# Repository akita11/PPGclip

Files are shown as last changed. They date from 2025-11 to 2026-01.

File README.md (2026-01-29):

# PPG Clip

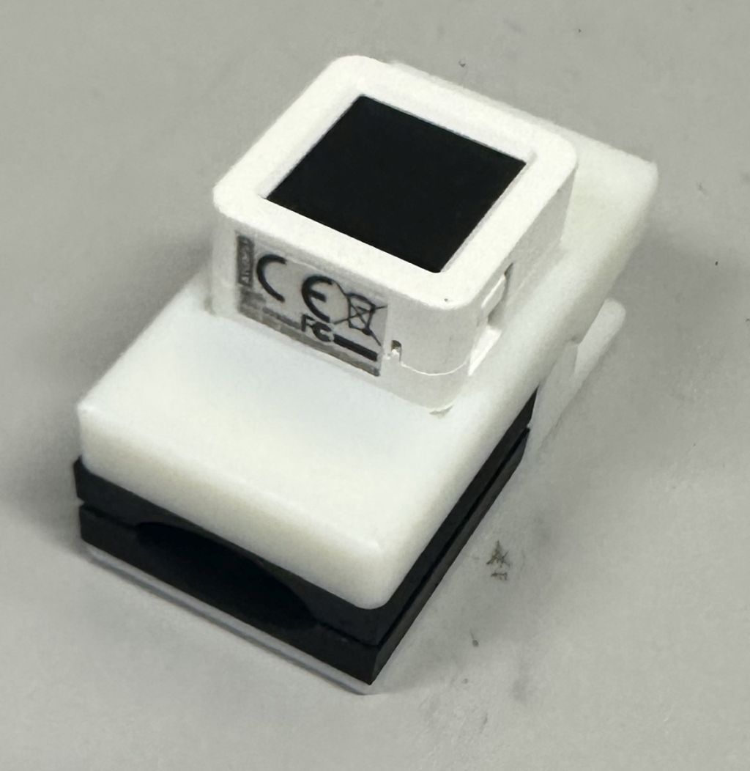
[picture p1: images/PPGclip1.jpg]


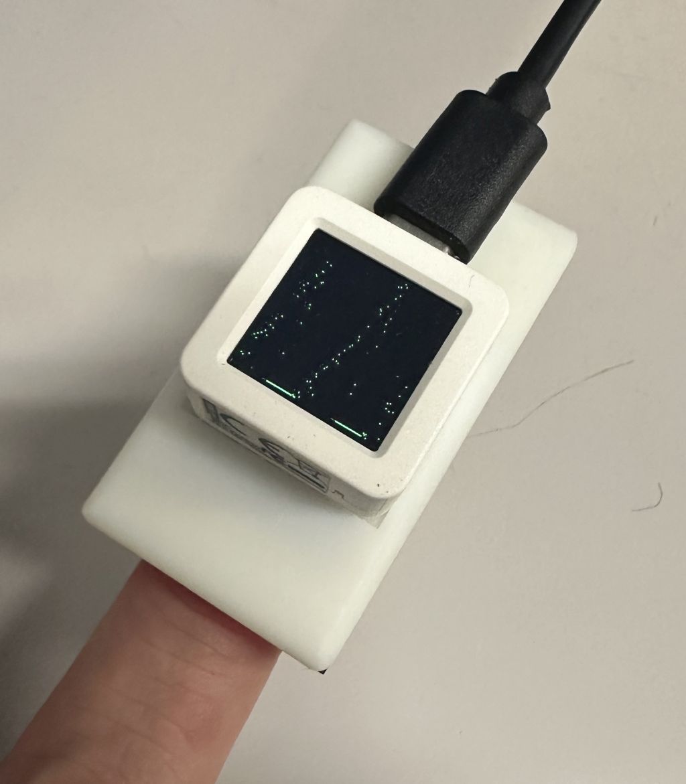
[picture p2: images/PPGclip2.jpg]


[M5Stack社の心拍センサユニット](https://www.switch-science.com/products/5695)を利用した、測定精度・安定度の高い透過型の光学脈波(PPG)計測器です。
マイコン部はM5Stack社のATOMシリーズを取り付けらて一体化できます。
部品セットからこれらを組み立てることができます。

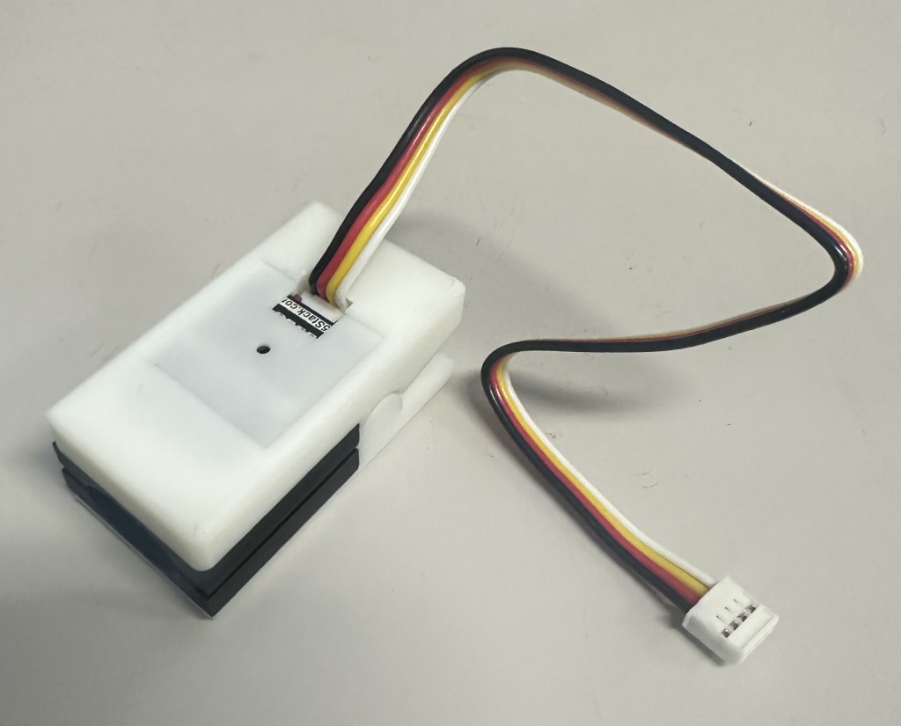
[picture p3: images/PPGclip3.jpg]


ATOMシリーズを使わずに、直接Groveケーブルを接続して、他のM5Stackシリーズ等のマイコンで使用することもできます。

## 必要なもの
- 部品セット（筐体（4点）、LED基板、コネクタ基板、4p/2mmピンソケット×2、ケーブル（色が写真のものと異なる場合があります）、M2.3×8mmタッピングねじ、M2×4mmねじ、押しバネ0.7×7.5×23）
- [M5Stack社の心拍センサユニット](https://www.switch-science.com/products/5695)
- M5Stack社ATOMシリーズ（ディスプレイのついている[ATOMS3](https://www.switch-science.com/products/8670)が脈波確認などができて便利。ATOMS3用のサンプルファームウエアあり）
- 工具（1.5mm六角レンチ、小プラスドライバ）

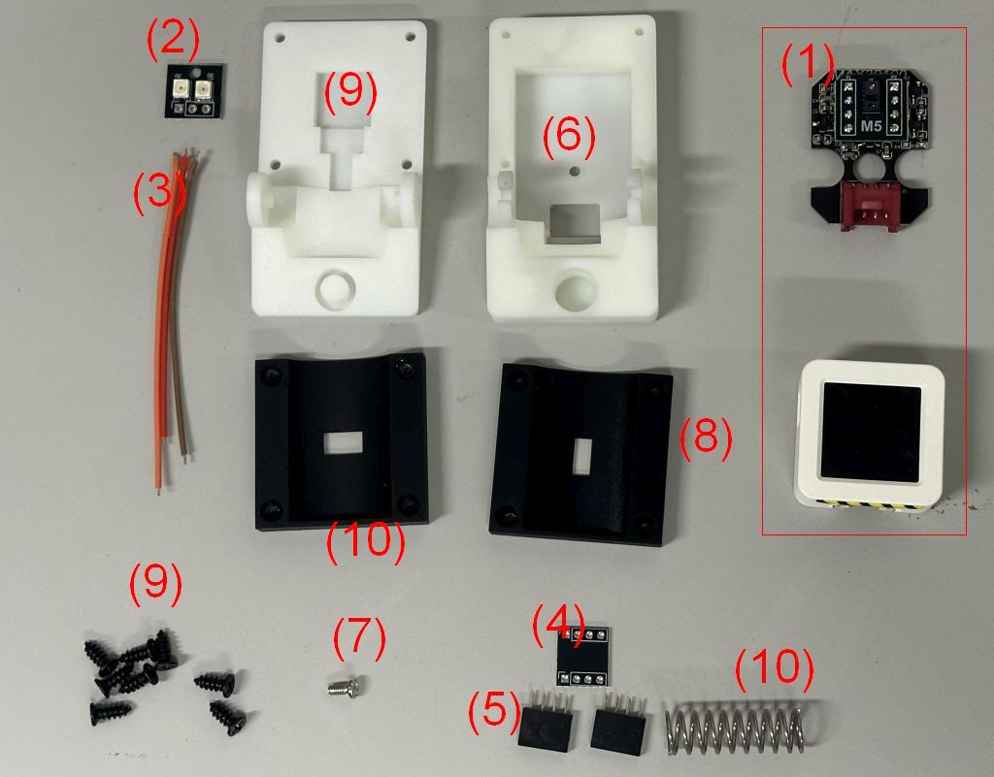
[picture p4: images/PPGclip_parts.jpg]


# 組み立て

1. 心拍センサユニットを、1.5mm六角レンチを使って分解し、中のボード(1)を取り出します。
1. LED基板(2)とボード(1)を、ケーブル(3)でFig1のようにはんだ付けして接続します。ケーブルの対応関係を間違えないように注意してください。このとき、ボード(1)側は、ケーブルを横側に引き出し、はんだづけ箇所がなるべく平坦になるようにします。
1. コネクタ基板(4)に、4p/2mmピンソケット(5)を2個、傾かないように注意してはんだ付けし、足をなるべく短くカットします。（Fig2）
1. ボード(1)にコネクタ基板(4)を差し込み、Fig3のように筐体(6）にはめます。ケーブル(3)は、図のように上面基板に重ならないようにします。
1. ATOMシリーズを、コネクタ基板(4)の反対側にさしこみ、M2ねじ(7)でFig3のように固定します。
1. 黒い筐体(8)を筐体(6)（向きに注意）に、4個のタッピングねじ(9)でFig4のように固定します。
1. 筐体(9)に、LED基板(2)をFig5のようにはめ、黒い筐体(10)（向きに注意）を、4個のタッピングねじ(9)でFig6のように固定します。
1. Fig7のように、ばね(10)を筐体(9)にはめ、その後、Fig8のように、ばね(10)を反対側の筐体(6)にはめつつ、2つの筐体を押し込んではめこみます。
1. ATOMシリーズにプログラムを書き込み、ボード(1)が動作すると、Fig9のように上下両側のLEDが点灯します。

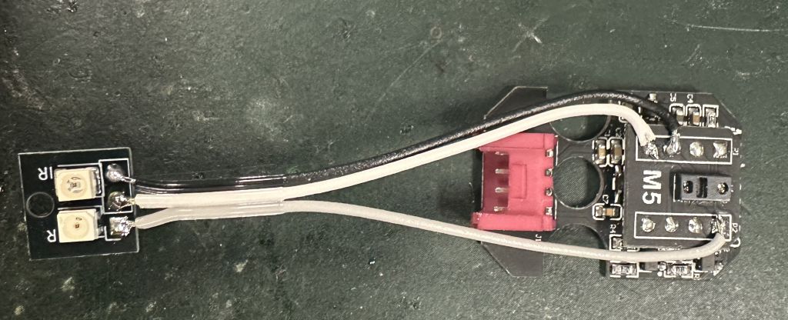
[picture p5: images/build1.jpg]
Fig1.:

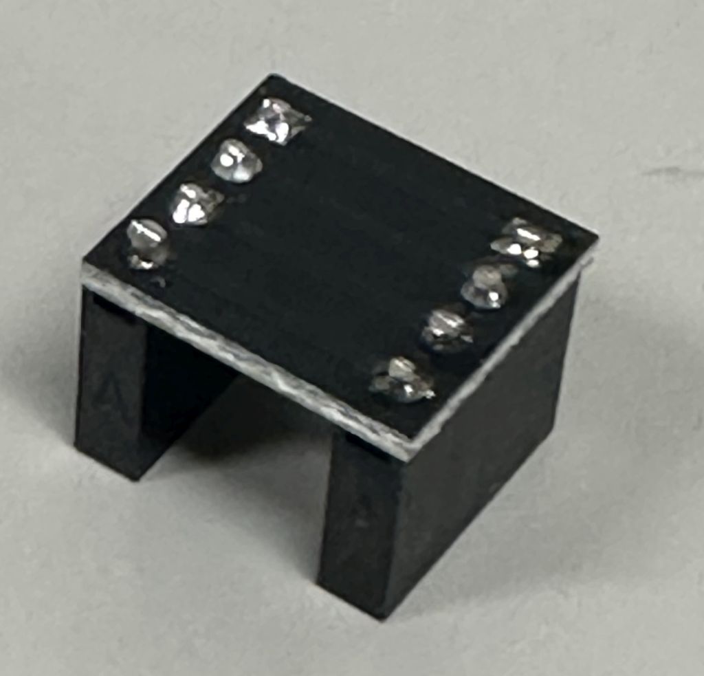
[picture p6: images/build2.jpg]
Fig2:

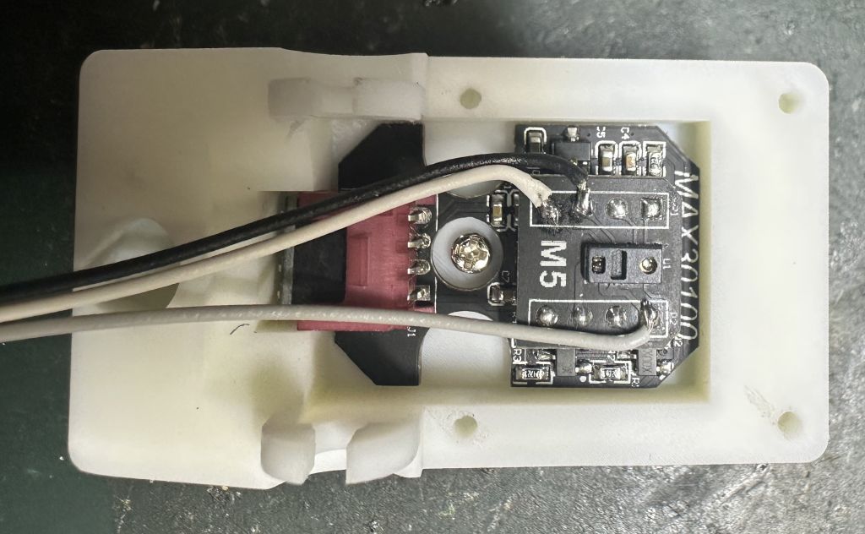
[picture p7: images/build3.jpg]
Fig3:

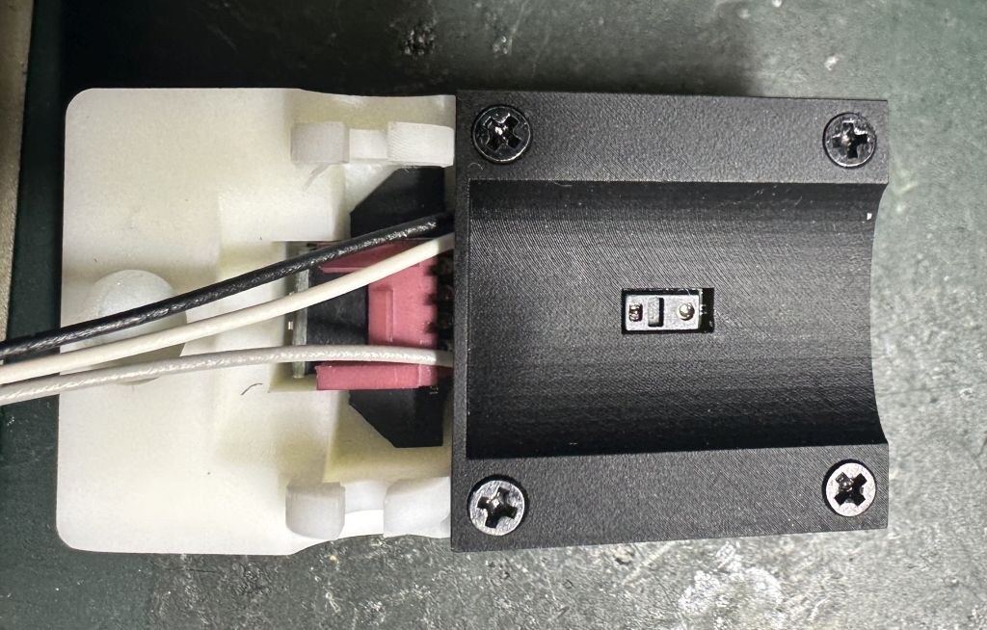
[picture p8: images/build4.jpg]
Fig4:

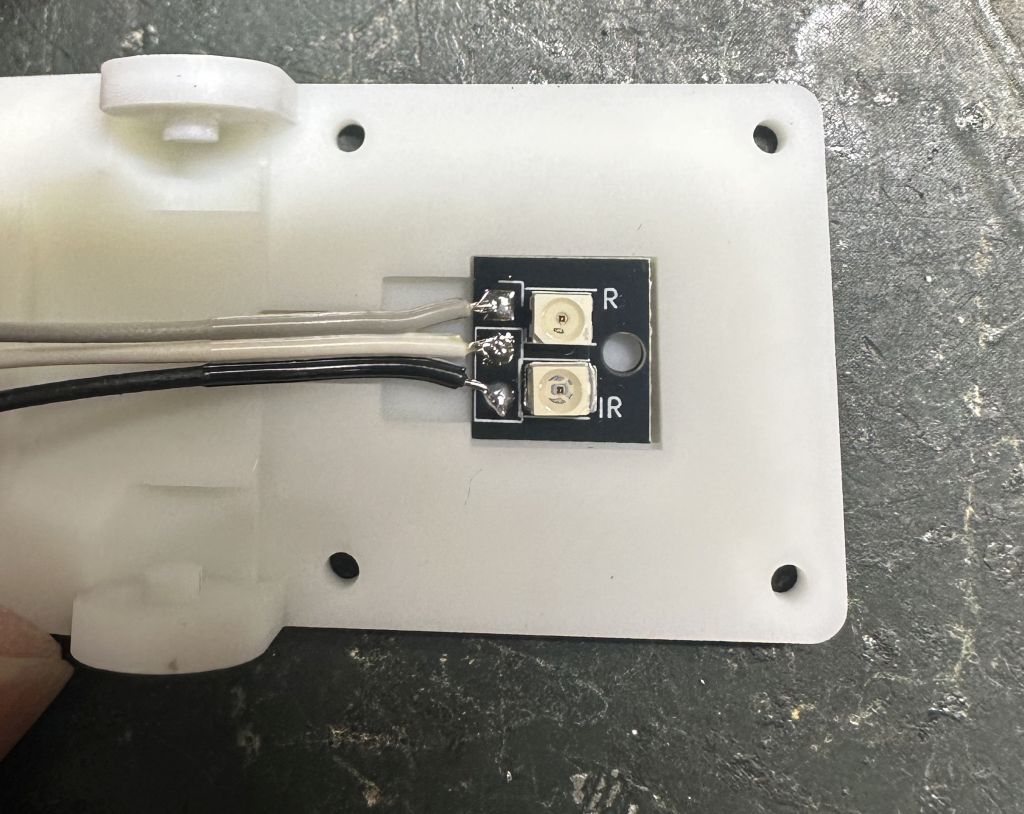
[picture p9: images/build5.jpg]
Fig5:

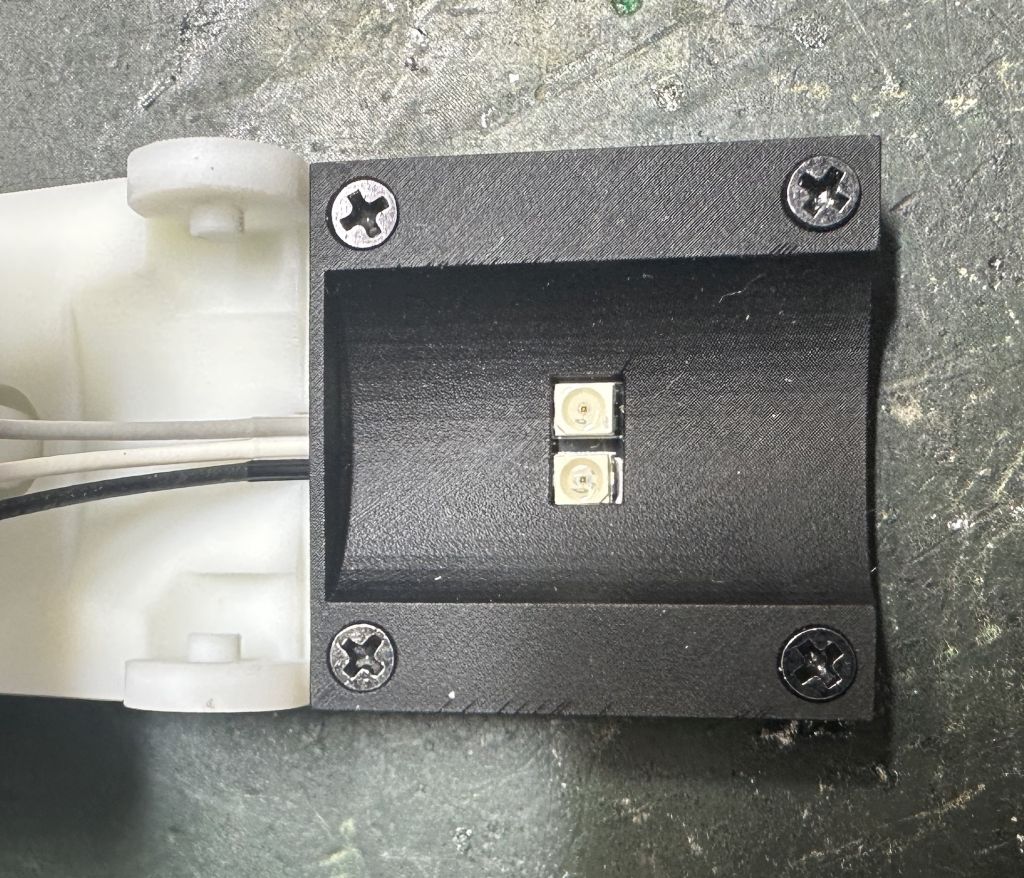
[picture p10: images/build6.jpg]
Fig6:

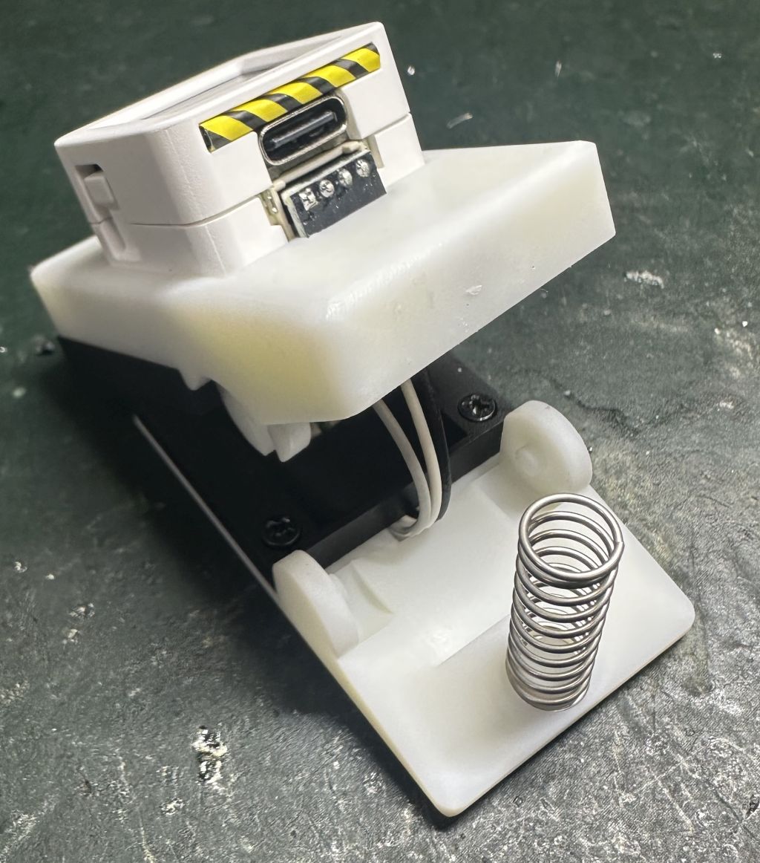
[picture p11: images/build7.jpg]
Fig7:

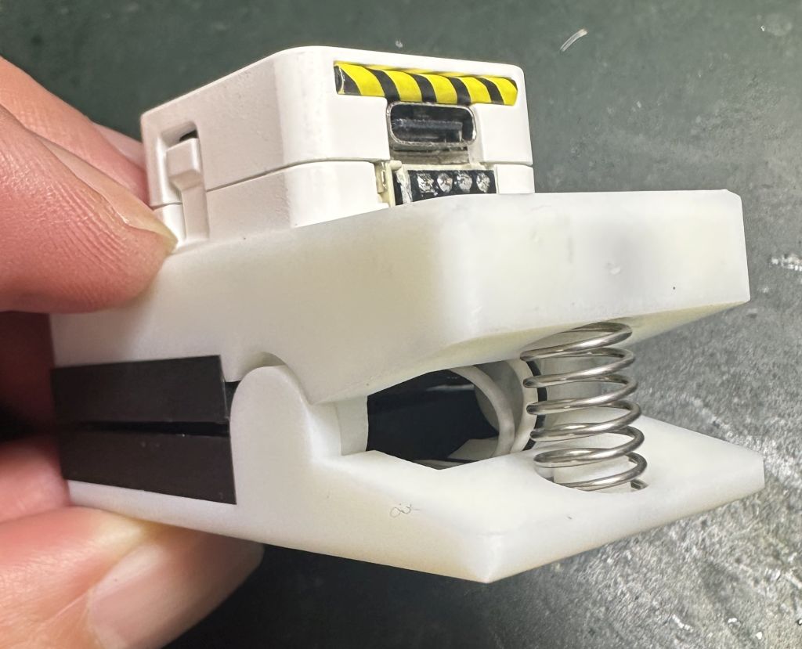
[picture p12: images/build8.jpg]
Fig8:

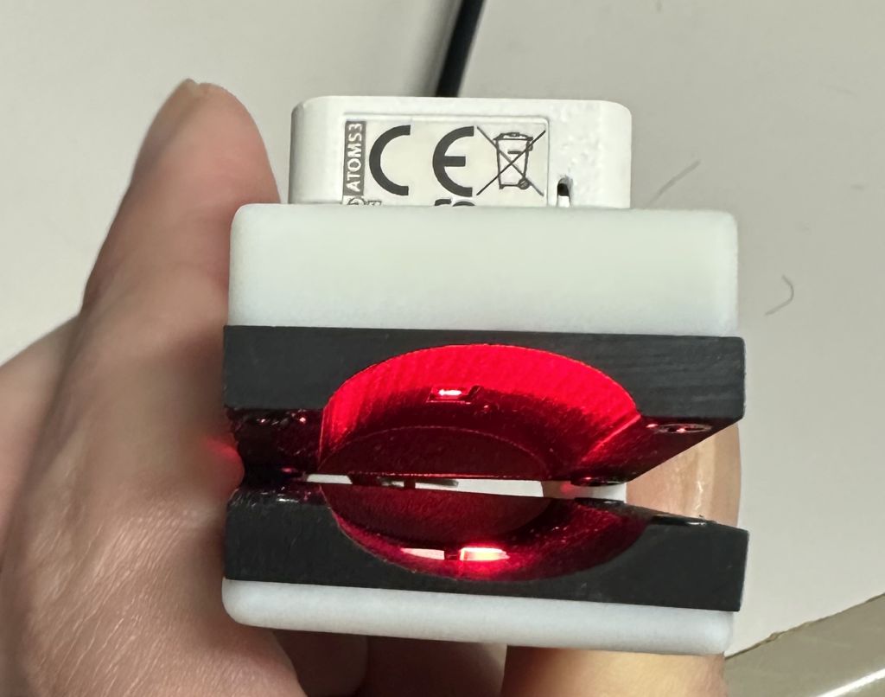
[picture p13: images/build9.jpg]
Fig9:

# ソフトウエア

M5Stack社の心拍センサユニット用のプログラムはすべて利用できます。サンプルとして、以下の機能をもつATOMS3用のプログラムがsampleFW/内にあります。
- 波形表示(100Hzサンプリング)
- ベースライン変動除去
- 簡易な正常計測チェック（正常計測時は緑色のグラフ）
- ボタンを押すと10秒分の生データをUSU UARTにCSV形式で出力

## Author

Junichi Akita (@akita11) / akita@ifdl.jp

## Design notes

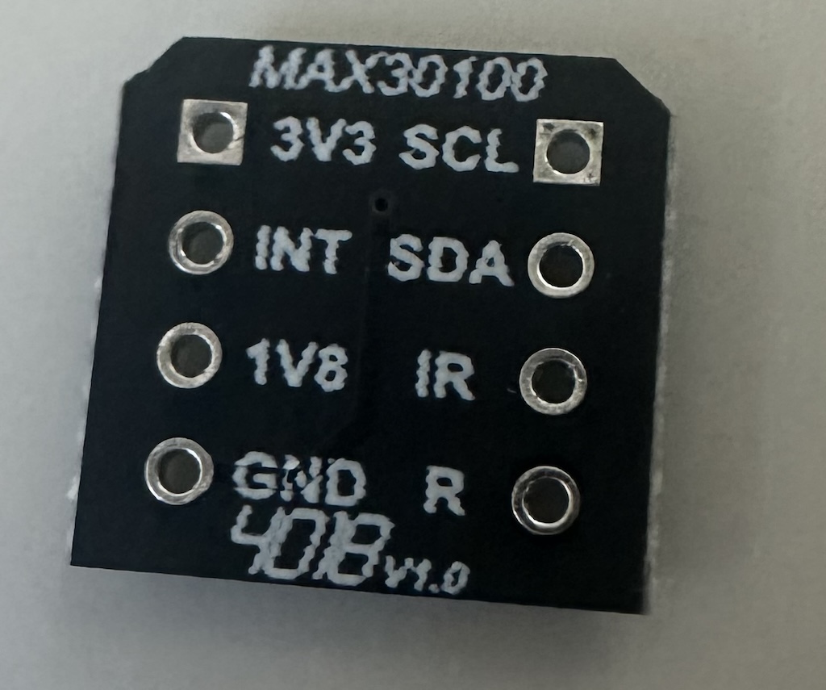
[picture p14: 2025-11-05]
images/HeartSensor_MAX30100sub.jpg

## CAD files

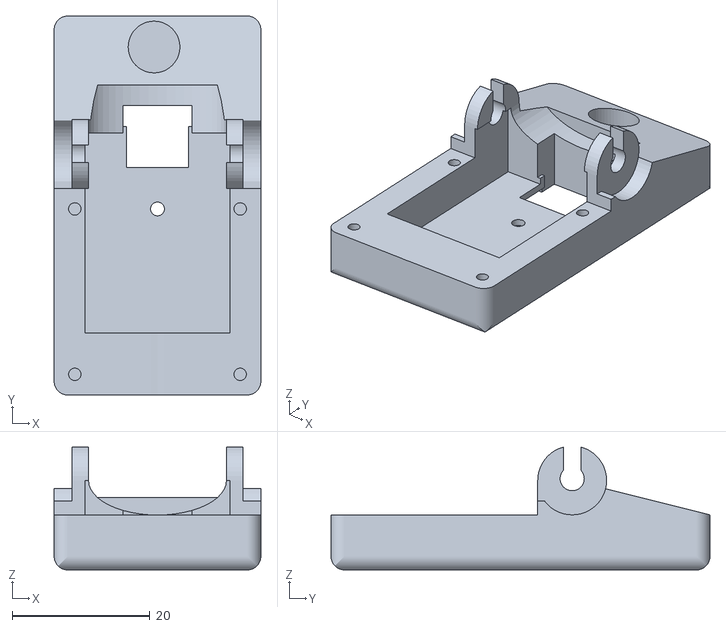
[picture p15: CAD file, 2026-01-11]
body/PPGclip1b.stl
30.0 x 55.0 x 17.8

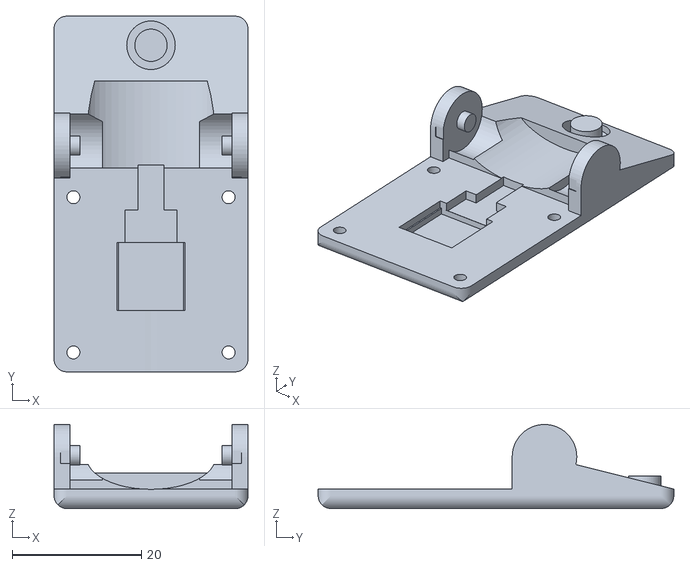
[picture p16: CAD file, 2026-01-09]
body/PPGclip2b.stl
30.0 x 55.0 x 13.0

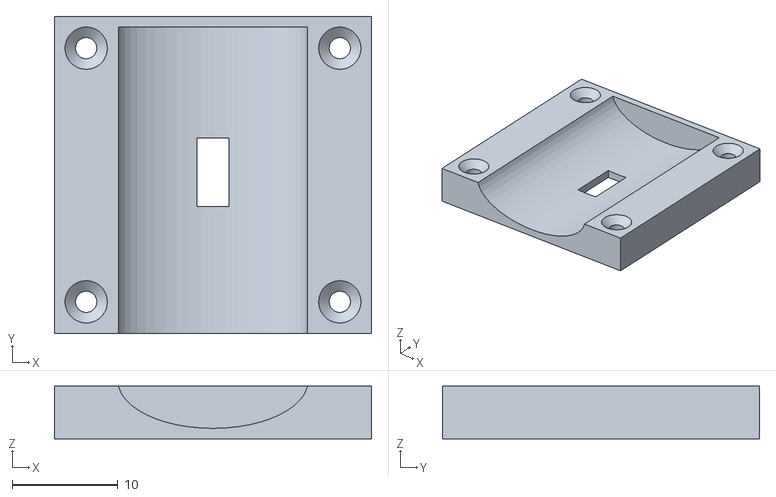
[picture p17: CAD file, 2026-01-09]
body/PPGclip1t.stl
30.0 x 30.0 x 5.00

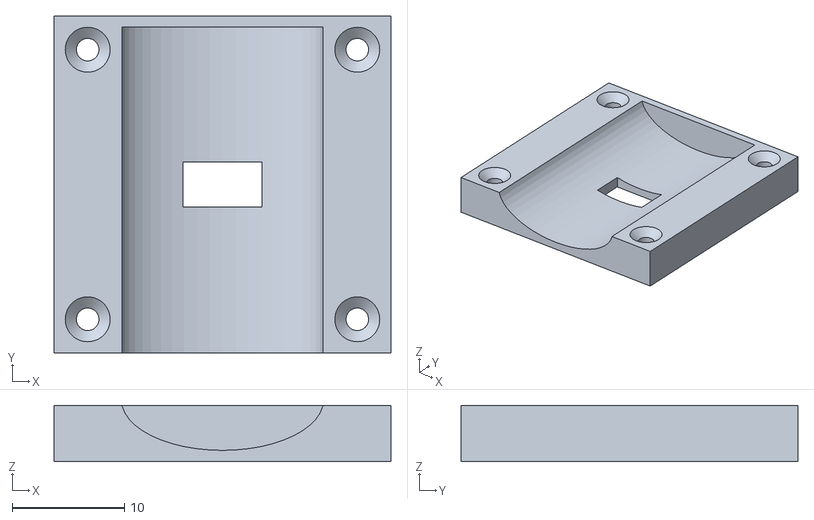
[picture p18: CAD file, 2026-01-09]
body/PPGclip2t.stl
30.0 x 30.0 x 5.00

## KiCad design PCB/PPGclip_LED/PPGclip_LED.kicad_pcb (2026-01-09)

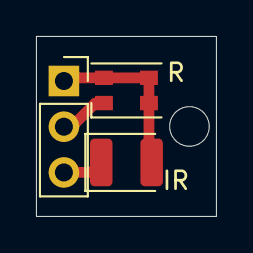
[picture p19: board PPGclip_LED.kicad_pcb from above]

Board: 2 copper layers, 10.0 x 10.0 mm, 3 parts (0 on the bottom side), 3 nets.

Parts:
D1: LED; LED_1210_3225Metric
D2: LED; LED_Cree-PLCC4_3.2x2.8mm_CCW
J1: Conn_01x03; PinSocket_1x03_P2.54mm_Vertical

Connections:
unnamed: D1.1 (K), J1.3
unnamed: D1.2 (A), D2.2 (A), J1.1
unnamed: D2.1 (K), J1.2

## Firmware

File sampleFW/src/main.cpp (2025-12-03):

#include <Arduino.h>
#include <M5unified.h>
#include <Wire.h>
#include <math.h>

#include "MAX30100.h"

// Sampling is tightly related to the dynamic range of the ADC.
// refer to the datasheet for further info
#define SAMPLING_RATE MAX30100_SAMPRATE_100HZ
//#define SAMPLING_RATE MAX30100_SAMPRATE_50HZ

// The LEDs currents must be set to a level that avoids clipping and maximises the
// dynamic range
#define IR_LED_CURRENT MAX30100_LED_CURR_50MA
#define RED_LED_CURRENT MAX30100_LED_CURR_27_1MA

// The pulse width of the LEDs driving determines the resolution of
// the ADC (which is a Sigma-Delta).
// set HIGHRES_MODE to true only when setting PULSE_WIDTH to MAX30100_SPC_PW_1600US_16BITS
#define PULSE_WIDTH MAX30100_SPC_PW_1600US_16BITS
#define HIGHRES_MODE true

// Instantiate a MAX30100 sensor class
MAX30100 sensor;

// --- フィルタ設定パラメータ (filterESP32.cから移植) ---
const int SAMPLE_RATE = 100;       // 100Hz
const int WINDOW_SIZE = 150;       // 1.5秒間のウィンドウ (相関・標準偏差計算用)
const int FILTER_ORDER = 4;        // フィルタ次数 + 1 (係数の数) -> 4次フィルタなら係数は5個

// --- フィルタ係数 (Pythonで計算した値をここに設定) ---
// Bandpass Filter (0.5 - 5.0 Hz), fs=100Hz, order=4
const float B_BPF[] = { 0.0006760592, 0.0000000000, -0.0013521185, 0.0000000000, 0.0006760592 };
const float A_BPF[] = { 1.0000000000, -3.6186414773, 4.9356346257, -3.0031317094, 0.6865261313 };

// Lowpass Filter (0.5 Hz) for Baseline, fs=100Hz, order=4
const float B_LPF[] = { 0.0000000570, 0.0000002281, 0.0000003422, 0.0000002281, 0.0000000570 };
const float A_LPF[] = { 1.0000000000, -3.9370720516, 5.8118005697, -3.8119614450, 0.9372338394 };

// --- PPGプロセッサクラス (filterESP32.cから移植) ---
class PPGProcessor {
private:
    // フィルタの状態変数 (直近の入出力を保持)
    float x_red[FILTER_ORDER + 1] = {0};
    float y_red[FILTER_ORDER + 1] = {0};
    float x_ir[FILTER_ORDER + 1] = {0};
    float y_ir[FILTER_ORDER + 1] = {0};
    
    // ベースライン用フィルタ状態変数
    float x_base[FILTER_ORDER + 1] = {0};
    float y_base[FILTER_ORDER + 1] = {0};

    // リングバッファ (判定計算用)
    float bufFiltRed[WINDOW_SIZE];
    float bufFiltIR[WINDOW_SIZE];
    float bufRawIR[WINDOW_SIZE]; // 接触判定用
    int bufIndex = 0;
    bool bufferFilled = false;

    // 前回のベースライン値 (傾き計算用)
    float prevBaseline = 0;
    
    // IIRフィルタ計算関数
    float applyIIR(float input, float* x, float* y, const float* b, const float* a) {
        // シフト処理
        for (int i = FILTER_ORDER; i > 0; i--) {
            x[i] = x[i - 1];
            y[i] = y[i - 1];
        }
        x[0] = input;

        // 差分方程式: y[0] = (b[0]x[0] + ... + b[N]x[N]) - (a[1]y[1] + ... + a[N]y[N])
        // a[0]は通常1.0なので省略
        float val = 0;
        for (int i = 0; i <= FILTER_ORDER; i++) {
            val += b[i] * x[i];
        }
        for (int i = 1; i <= FILTER_ORDER; i++) {
            val -= a[i] * y[i];
        }
        y[0] = val;
        return val;
    }

public:
    struct PPGResult {
        float filtRed;
        float filtIR;
        int qualityFlag; // 1: Valid, 0: Invalid
    };

    PPGProcessor() {
        // バッファ初期化
        for(int i=0; i<WINDOW_SIZE; i++) {
            bufFiltRed[i] = 0;
            bufFiltIR[i] = 0;
            bufRawIR[i] = 0;
        }
    }

    // 毎サンプリング呼び出す関数
    PPGResult update(float rawRed, float rawIR) {
        PPGResult res;

        // 1. バンドパスフィルタ適用 (脈波抽出)
        res.filtRed = applyIIR(rawRed, x_red, y_red, B_BPF, A_BPF);
        res.filtIR = applyIIR(rawIR, x_ir, y_ir, B_BPF, A_BPF);

        // 2. ローパスフィルタ適用 (ベースライン抽出 for IR)
        float baselineIR = applyIIR(rawIR, x_base, y_base, B_LPF, A_LPF);

        // 3. バッファにデータを追加 (リングバッファ)
        bufFiltRed[bufIndex] = res.filtRed;
        bufFiltIR[bufIndex] = res.filtIR;
        bufRawIR[bufIndex] = rawIR;

        // 4. ベースライン変動チェック (傾き)
        float slope = abs(baselineIR - prevBaseline); // 簡易微分
        prevBaseline = baselineIR;

        // --- 品質判定ロジック ---
        // まだバッファが埋まっていない場合は判定しない(0)
        if (!bufferFilled && bufIndex < WINDOW_SIZE - 1) {
            res.qualityFlag = 0;
        } else {
            // リングバッファが一周したらフラグを立てる
            if (bufIndex == WINDOW_SIZE - 1) bufferFilled = true;

            // 統計計算 (平均、標準偏差、共分散)
            float sumRed = 0, sumIR = 0;
            float sumRedSq = 0, sumIRSq = 0;
            float sumCross = 0;
            float minRawIR = 1000000; // Rawデータの最小値チェック用

            for (int i = 0; i < WINDOW_SIZE; i++) {
                float r = bufFiltRed[i];
                float ir = bufFiltIR[i];
                float raw = bufRawIR[i];

                sumRed += r;
                sumIR += ir;
                sumRedSq += r * r;
                sumIRSq += ir * ir;
                sumCross += r * ir;
                if (raw < minRawIR) minRawIR = raw;
            }

            float meanRed = sumRed / WINDOW_SIZE;
            float meanIR = sumIR / WINDOW_SIZE;
            
            // 分散・共分散
            // Var(X) = E[X^2] - (E[X])^2
            float varRed = (sumRedSq / WINDOW_SIZE) - (meanRed * meanRed);
            float varIR = (sumIRSq / WINDOW_SIZE) - (meanIR * meanIR);
            float cov = (sumCross / WINDOW_SIZE) - (meanRed * meanIR);
            
            float stdRed = sqrt(varRed > 0 ? varRed : 0);
            float stdIR = sqrt(varIR > 0 ? varIR : 0);

            // 相関係数
            float correlation = 0;
            if (stdRed > 0 && stdIR > 0) {
                correlation = cov / (stdRed * stdIR);
            }

            // 判定条件 (Pythonコード準拠)
            // 1. 相関 > 0.8
            // 2. 振幅(stdIR) > 5.0
            // 3. Raw値(接触) > 10000 (ここではバッファ内の最小値で判定)
            // 4. ベースライン傾き < 10.0 (現在の傾きを使用)
            
            bool isCorrOK = correlation > 0.8;
            bool isAmpOK = stdIR > 1.3;
            bool isContactOK = minRawIR > 10000;
            bool isStable = slope < 10.0; // 閾値はサンプリングレートやゲインによるので要調整
//            if (isCorrOK && isAmpOK && isContactOK && isStable) {
            if (isCorrOK && isAmpOK && isContactOK) {
                res.qualityFlag = 1;
            } else {
                res.qualityFlag = 0;
            }
//            printf("%d : %d %d (%.2f) %d %d(%.2f / %.2f %.2f)\n", res.qualityFlag, isCorrOK, isAmpOK, stdIR, isContactOK, isStable, slope, baselineIR, prevBaseline);
        }

        // インデックス更新
        bufIndex++;
        if (bufIndex >= WINDOW_SIZE) bufIndex = 0;

        return res;
    }
    
    // リセット関数 (ボタン押下時用)
    void reset() {
        for (int i = 0; i <= FILTER_ORDER; i++) {
            x_red[i] = 0;
            y_red[i] = 0;
            x_ir[i] = 0;
            y_ir[i] = 0;
            x_base[i] = 0;
            y_base[i] = 0;
        }
        for(int i=0; i<WINDOW_SIZE; i++) {
            bufFiltRed[i] = 0;
            bufFiltIR[i] = 0;
            bufRawIR[i] = 0;
        }
        bufIndex = 0;
        bufferFilled = false;
        prevBaseline = 0;
    }
};

// PPGプロセッサのインスタンス
PPGProcessor ppgProcessor;

// display: 128 x 128 (M5Stack ATOMS3)
#define X 128
#define Y 128
#define N 128
#define Nbit 7

uint16_t val_red[N], val_ir[N];
uint8_t px = 0;

// リングバッファ: 60秒分（6000サンプル、100Hz）のデータを保存
// メモリ制約のため、実際のサンプリングレートに合わせて6000サンプルに設定
#define BUFFER_SIZE 6000
struct DataSample {
  uint16_t red;         // 生データ (Red)
  uint16_t ir;          // 生データ (IR)
  float filtRed;        // フィルタ後のデータ (Red)
  float filtIR;         // フィルタ後のデータ (IR)
  uint16_t timestamp;   // タイムスタンプ（ms、65535ms = 65秒まで対応可能）
};
DataSample dataBuffer[BUFFER_SIZE];
uint32_t bufferIndex = 0;
uint32_t sampleCount = 0; // 保存されたサンプル数
uint32_t timeBase = 0; // タイムスタンプの基準時刻（起動時または前回のUART転送終了時）
int currentQualityFlag = 0; // 現在の品質フラグ (グラフ描画用)

#define Navg_base 100
#define Navg_data 10
#define Navg_slope 10
int data0 = 0;
uint8_t fRamp = 0, fRamp0 = 0;
int slope[Navg_slope];
uint8_t pSlope = 0;
uint16_t tNP = 0, tPN = 0, tPN0 = 0, periodPN = 0, periodNP = 0;
uint8_t fValid = 0;
uint32_t sum_base = 0, sum_data = 0;
long sum_slope = 0;

void setup()
{
  // I2CピンをGroveコネクタのGPIO1(SCL)とGPIO2(SDA)に設定
  Wire.setPins(2, 1); // SDA=GPIO2, SCL=GPIO1
  Wire.begin();
  
  M5.begin();

  if (!sensor.begin())
  {
    printf("fail\n");
    for (;;)
      ;
  }
  else
  {
    printf("ok\n");
  }

  // Set up the wanted parameters
  sensor.setMode(MAX30100_MODE_SPO2_HR);
  sensor.setLedsCurrent(IR_LED_CURRENT, RED_LED_CURRENT);
  sensor.setLedsPulseWidth(PULSE_WIDTH);
  sensor.setSamplingRate(SAMPLING_RATE);
  sensor.setHighresModeEnabled(HIGHRES_MODE);
  M5.Lcd.clear();
  for (uint16_t x = 0; x < N; x++)
  {
    val_red[x] = 0;
    val_ir[x] = 0;
  }
  
  // リングバッファの初期化
  for (uint32_t i = 0; i < BUFFER_SIZE; i++)
  {
    dataBuffer[i].red = 0;
    dataBuffer[i].ir = 0;
    dataBuffer[i].filtRed = 0;
    dataBuffer[i].filtIR = 0;
    dataBuffer[i].timestamp = 0;
  }
  bufferIndex = 0;
  sampleCount = 0;
  currentQualityFlag = 0;
  
  // 基準時刻を設定（起動時をt=0とする）
  timeBase = millis();
  
  printf("Data buffer initialized. Press button to export data.\n");
}

uint8_t f = 0;
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

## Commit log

2025-12-02 add filtering&valid check (not tested)
2025-12-03 filter&validation works (slope not checked)
2026-01-09 add STL&PCB
    [PPGclip1b.stl, PPGclip1t.stl, PPGclip2b.stl, PPGclip2t.stl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]
2026-01-11 STL fix
    [PPGclip1b.stl]
2026-01-28 add photo with Grove cable
